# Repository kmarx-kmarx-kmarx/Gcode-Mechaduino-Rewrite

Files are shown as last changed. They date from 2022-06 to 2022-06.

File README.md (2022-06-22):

## Poseidon Prime Firmware and Hardware
Poseidon prime is an open source and low cost syringe pump that uses off-the-shelf parts, 3D printed components, and free software which altogether costs a tenth of other syringe pumps. The design is open-source so anybody can download, modify, and make their own poseidon prime. The syringe pump is highly customizable and can be mounted to rails for extra stability, 3D printed out of polypropylene for heat resistance, and adjusted to fit a variety of syringe sizes. Poseidon prime currently can perform basic fluid dispensing tasks, but going forward it will be able to perform more complex operations and undergo rigorous testing to verify its precision and reliability.

This project builds on [poseidon](https://github.com/pachterlab/poseidon), a project from the Pachter lab. Poseidon prime improves the firmware by adding feedback control and G-code support and builds on the hardware with autoclave-safe polypropylene and a metal shell.

To control poseidon prime, we are using the [Mechaduino](https://github.com/jcchurch13/Mechaduino-Hardware) development board. The Mechaduino repo has the PCB files, BOM, and more information on the project. We found some parts utilized by the Mechaduino project were no longer in stock so we included a new BOM with links to products in stock. 

### The Pump:
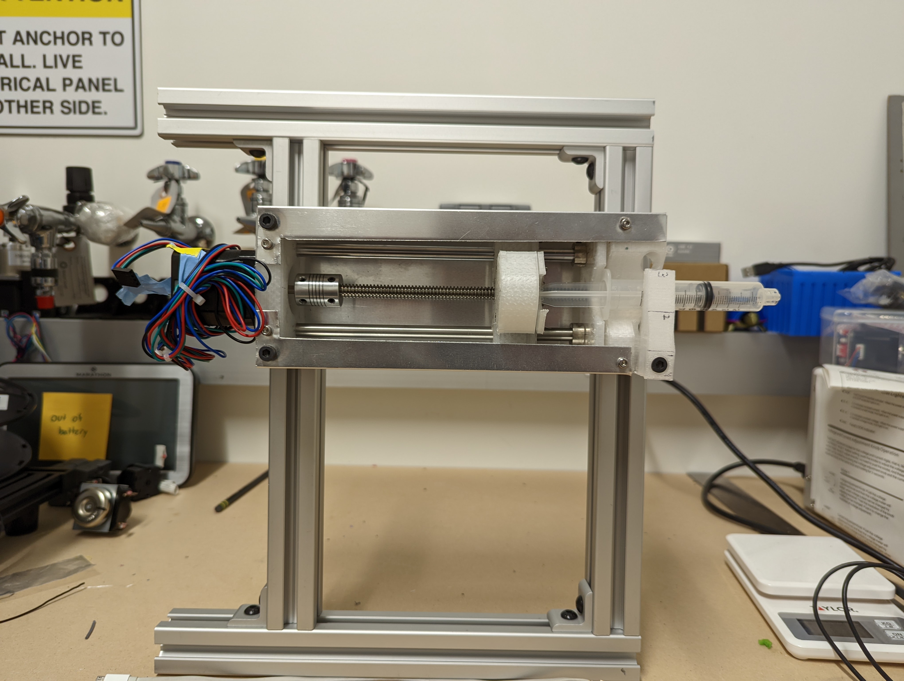
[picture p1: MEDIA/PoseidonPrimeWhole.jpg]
poseidon prime


## What's Included in this Repo
- `Tuning_and_debugging.md`: Guide for tuning and debugging the system
- Supporting Docs
	- `Sine Lookup.ipynb`: Jupyter notebook for generating a sine lookup table
	- `Velocity Lookup.ipynb`: Jupyter notebook for velocity lookup table proof-of-concept
- HARDWARE
	- `poseidon-prime v123.f3z`: Fusion 360 design file for poseidon prime
	- `p_prime_bom.csv`: Bill of Materials for poseidon prime
	- `mecha_bom.csv`: Bill of Materials for Mechaduino.
	- Design Files
		- `p_prime.stl`: STL file for the entire project
		- `back_block.stl`
		- `front_block.stl`
		- `front_clamp.stl`
		- `front_ear_holder.stl`
		- `small_syringe_press.stl`
		- `carriage_block.stl`
		- `carriage_block_cap.stl`
		- `enclosure.dxf`: DXF for the sheet metal enclosure
- Gcode-Mechaduino-Rewrite
	- `pseudocode.txt`: Basic overview of code operation
	- `Gcode-Mechaduino-Rewrite.ino`: Arduino sketch for the project
	- `MagneticEncoder.cpp`, `MagneticEncoder.h`: Files for communicating with the magnetic encoder
	- `MotorCtrl.cpp`, `MotorCtrl.h`: Files for interacting with the motor driver
	- `SerialCommand.cpp`, `SerialCommand.h`: Files for sending and recieving serial communications
	- `ProcessCmd.cpp`, `ProcessCmd.h`: Files for parsing the commands
	- `TimeControlInt.cpp`, `TimeControlInt.h`: Files for initializing and operating the control loops
	- `fastPWM.c`, `fastPWM.h`: Implement a higher frequency PWM
- MEDIA
	- `1CarriageBlockAssembly.mp4`: Video of assembling the carriage block. Perform this step first when building poseidon prime
	- `1CarriageBlockParts.jpg`: Still image of the parts necessary for assembling the carriage block
	- `2FrontBlockParts.jpg`: The parts of the front block
	- `3BackBlockParts.jpg`
	- `4EnclosureParts.jpg`
	- `PoseidonPrimeWhole.jpg`: View of the whole poseidon prime when mounted on rails
	- `PoseidonPrimeTip.jpg`: Close up on syringe end

Poseidon prime uses the Mechaduino microcontroller; see [the Mechaduino project GitHub](https://github.com/jcchurch13/Mechaduino-Hardware) for the BOM.

## Getting Started
### 3D Printing Components and Purchasing Components
See the BOMs for components, estimated prices, and where to purchase. 

The poseidon prime body could be printed in PLA, but PLA will deform and become brittle in an autoclave. It is advised to print usig polypropylene with a relatively high number of walls to ensure no water can enter the blocks. 

### Build Videos
See the [build videos](https://drive.google.com/drive/folders/1_DpoKlkosWUYHRFKvAd-3BIp1i3CB5ML?usp=sharing) for a guide on how to build poseidon prime.

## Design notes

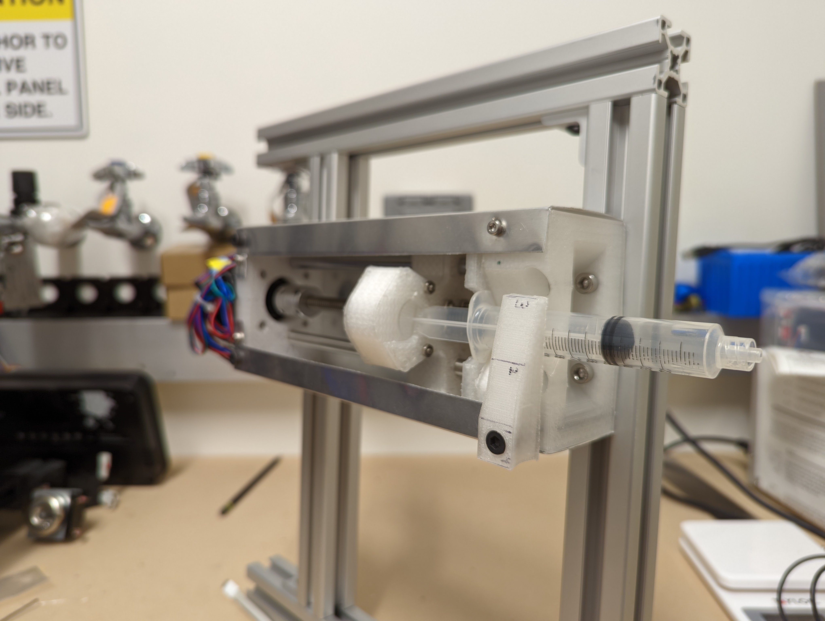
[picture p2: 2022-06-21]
MEDIA/PoseidonPrimeTip.jpg

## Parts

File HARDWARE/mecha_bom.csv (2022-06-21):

Qty (per board) | URL to purchase | Value | Device | Package | Parts | Description
1 | https://www.mouser.com/ProductDetail/onsemi/MBR0520LT1G?qs=3JMERSakebqBWTiPUQp0nw%3D%3D |  | DIODE_SOD-123 | SOD-123 | D1 | Library: MF_Discrete_Semiconductor
4 | DNP |  | HEADER_01X03_PTH_2.54MM | PTH_2.54MM_01X03 | 3V3, GND, V+, VIN | Library: MF_Connectors
1 | DNP |  | HEADER_01X06_PTH_2.54MM | PTH_2.54MM_01X06 | J3 | Library: MF_Connectors
1 | DNP |  | HEADER_01X10_PTH_2.54MM | PTH_2.54MM_01X10 | J2 | Library: MF_Connectors
1 | https://www.mouser.com/ProductDetail/Phoenix-Contact/1935161?qs=W3wJikR1%252BS6eKzfFl8Rbew%3D%3D |  | M025MM | SCREWTERMINAL-5MM-2 | MOTOR_POWER | Standard 2-pin 0.1 header. Use with
1 | https://www.mouser.com/ProductDetail/Amphenol-Commercial-Products/G800W304018EU?qs=f9yNj16SXrKi9QS16pMdvA%3D%3D |  | M04PTH | 1X04 | JP6 | Header 4
1 | https://www.mouser.com/ProductDetail/CK/RKB2SJG250SMTR-LFS?qs=iLbezkQI%252Bsgsc0TY%2FPaT8A%3D%3D |  | TACT_4.2MM | TACT4.2MM | SW2 | Library: MF_Switches
1 | https://www.mouser.com/ProductDetail/Amphenol-FCI/10118193-0001LF |  | USB_MICRO_RIGHT | MICROUSB-RIGHT | J1 | Library: MF_Connectors
2 | https://www.mouser.com/ProductDetail/Susumu/KRL1632E-M-R150-F-T5?qs=B%2FFHBzrwtkbqYiRFE1Q74A%3D%3D | .15 Ohm | R-US_R1206 | R1206 | R12, R13 | RESISTOR
1 | https://www.mouser.com/ProductDetail/Murata-Electronics/GCM155R71H103KA55D?qs=aEuGZpxfbxUFaK62TPaKIA%3D%3D | 0.01uF | CAP0402 | 0402-CAP | C6 | Capacitor
8 | https://www.mouser.com/ProductDetail/Murata-Electronics/GCM155R71A104KA55D?qs=dNBNMwHp2UBmrB9ORE%252B4fA%3D%3D | 0.1uF | CAP0402 | 0402-CAP | C1, C2, C3, C4, C5, C14, C15, C16 | Capacitor
3 | https://www.mouser.com/ProductDetail/Murata-Electronics/GRM155R61C105KA12D?qs=MNX0Jdkv8mRzFdIwfsySnw%3D%3D | 1.0uF | CAP0402 | 0402-CAP | C9, C19 | Capacitor
1 | https://www.mouser.com/ProductDetail/Murata-Electronics/GRT188R61H105KE13D?qs=drgMNd%252BkGPNIxxtJByMGCg%3D%3D | 1.0uF | CAP0603 | 0603-CAP | C13 | Capacitor
1 | https://www.mouser.com/ProductDetail/YAGEO/RC0402FR-13100KL?qs=sGAEpiMZZMvdGkrng054t8AJgcdMkx7x5wItdGYa6aA%3D | 100K | R-US_R0402-VISHAY | R0402-VISHAY | R16 | RESISTOR
1 | https://www.digikey.com/en/products/detail/nichicon/RSA1E101MCN1GS/9452667 | 100uF | CAP_POLD |  | C12 | Capacitor Polarized
8 | https://www.mouser.com/ProductDetail/YAGEO/AC0402JR-0710KL | 10K | R-US_R0402-VISHAY | R0402-VISHAY | R1, R2, R3. R4, R6, R11, R20, R21 | RESISTOR
2 | https://www.mouser.com/ProductDetail/Murata-Electronics/GCM1555C1H180FA16D?qs=QzBtWTOodeXF93Udjj87vw%3D%3D | 18pF | CAP0402 | 0402-CAP | C7, C8 | Capacitor
2 | https://www.mouser.com/ProductDetail/YAGEO/AC0402FR-131KL | 1k | R-US_R0402-VISHAY | R0402-VISHAY | R14, R15 | RESISTOR
1 | https://www.digikey.com/en/products/detail/micro-crystal-ag/CM8V-T1A-32-768KHZ-7PF-20PPM-TA-QC/10499080 | 32768Khz | CRYSTAL2013 | CRYSTAL-SMD-2.0X1.3 | Y1 | Crystal
1 | https://www.mouser.com/ProductDetail/YAGEO/RC0402JR-07330RL | 330 | R-US_R0402-VISHAY | R0402-VISHAY | R5 | RESISTOR
2 | https://www.mouser.com/ProductDetail/YAGEO/RC0402JR-074K7L | 4.7K | R-US_R0402-VISHAY | R0402-VISHAY | R7, R8 | RESISTOR
1 | https://www.mouser.com/ProductDetail/Littelfuse/1206L025YR?qs=PWhpLWeW8wedgRREX8zxcg%3D%3D | 500mA | PTCSMD | PTC-1206 | F1 | Resettable Fuse PTC
1 | https://www.mouser.com/ProductDetail/ams/AS5047D-ATSM | AS5047D | AS5047D | TSSOP14 | U$4
1 | https://www.digikey.com/en/products/detail/allegro-microsystems/A4954ELPTR-T/2509910?lang=en&s=N4IgTCBcDaIIYBYCcBWBIC6BfIA&site=us&x=20&y=17 | AVAGO_DRIVERTHERM | AVAGO_DRIVERTHERM | TSSOP16_THERM | U$1
2 | https://www.digikey.com/en/products/detail/shenzhen-sunlord-electronics-co-ltd/PZ1608U471-1R0TF/14120402 | BLM18PG471SN1D | INDUCTOR0603-TDK | 0603-TDK | L1, L2 | Inductors
4 | https://www.mouser.com/ProductDetail/Nexperia/BSS138P215?qs=A1cBxND5mHJyVAOcRahidg%3D%3D | BSS138 | MOSFET-NCHANNELSMD | SOT23-3 | Q1, Q3, Q4, Q5 | NFET
1 | DNE | FRAME-LEDGER | FRAME-LEDGER | CREATIVE_COMMONS | FRAME1 | Schematic Frame
1 | https://www.mouser.com/ProductDetail/Kingbright/APTD2012LCGCK?qs=AQlKX63v8RvNHN%2F9EGvNTg%3D%3D | Green | 0044_KPT-2012YC | CHIPLED_0805 | LED1 | LED YELLOW - SMD - 0805
1 | DNE | MECHADUINO_LOGO | MECHADUINO_LOGO | MECHADUINO_LOGO | U$5
1 | DNE | NEMA17_HOLE_PATTERNNEW | NEMA17_HOLE_PATTERNNEW | NEMA17_HOLE_PATTERN_2 | U$2
1 | https://www.mouser.com/ProductDetail/Nexperia/2N7002PW115?qs=8%252BCzCWLBsnDY2xJ5Ehsi7w%3D%3D | NFET | MOSFET-NCHANNEL2N7002PW | SOT323 | Q2 | Common NMOSFET Parts
1 | DNE | OSHW-LOGOMOD | OSHW-LOGOMOD | OSHW_LOGO_COPPER_MOD | LOGO4 | Open Source Hardware Logo
1 | https://www.mouser.com/ProductDetail/Microchip-Technology-Atmel/ATSAMD21G18A-AUT | SAMD21G18A-AUT | INTEGRATEDCIRCUITS_1792_SAMD21G18A-AUT | INTEGRATEDCIRCUITS_TQFP48-7X7 | IC1 | Atmel D21 32bit ARM Cortex-M0 microcontroller - 48 PIN TQFP
1 | DNP | SHORT-HA5 | SHORT-HA5 | SHORT_ALL-50 | SH1 | Short between two nets
1 | DNP | SWD | CONNETTORI_0171_PH127-205DF055G00A | CONNETTORI_PINHEAD-2X5-P127 | JP4 | 2x5 PASSO 1
1 | https://www.mouser.com/ProductDetail/STMicroelectronics/LDK130M33RY?qs=1mbolxNpo8eOrhac%2FeIeAA%3D%3D | LDK130M33RY | LDK130M33RY | SOT-23-5 | U1 | 3v3 LDO
1 | DNE | TROPICAL_LABS_LOGO_1LOGO3 | TROPICAL_LABS_LOGO_1LOGO3 | LOGO3 | U$3
1 | https://www.kjmagnetics.com/proddetail.asp?prod=D42DIA&cat=8 | Diametrically magnetized magnet

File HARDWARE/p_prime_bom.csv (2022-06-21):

Quantity | URL to purchase | Cost (USD) | Item | Use | Description
1 | 3D printed | ~ | Back Block | 1x in back block assembly | The back block for connecting to the motor
1 | 3D printed | ~ | Front Block | 1x in front block assembly | The front block for holding the syringe and rails
1 | 3D printed | ~ | Ear Holder | 1x in front block assembly | Holds the ears of the syringe so it doesn't slide along the axis of motion
1 | 3D printed | ~ | Clamp | 1x in front block assembly | Holds the syringe down
1 | 3D printed | ~ | Carriage | 1x in carriage assembly | Presses against the plunger to push liquid out
1 | 3D printed | ~ | Carriage Cap | 1x in carriage assembly | Pulls against the plunger to pull liquid in
1 | https://www.mcmaster.com/8973K298-8973K302/ | $7.90 | 12"x12" Aluminum Sheet 0.0250" Thick | 1x in enclousure | Sheet metal wraps around the whole device for added stability
3 | https://www.mcmaster.com/91292A197 | $1.50 | M5x60 socket head cap screw | 2x in enclosure, 1x in front block | Holds the back block to the rails in the enclosure, attaches the clamp to the front block in the front block assembly
2 | https://www.mcmaster.com/91292A128 | $0.33 | M5x20 socket head cap screw | 2x in enclosure | Holds the front block to the rails
4 | https://www.mcmaster.com/6000N133/ | $5.20 | M5 T-Slotted Framing Fasteners | 4x in enclosure | Holds poseidon prime to the rails
4 |  |  | M3 10 mm socket head cap screw | 4x in enclosure | Holds enclosure sheet metal onto body
4 |  |  | M3 14 mm socket head cap screw | 4x in back block | Holds motor to back block
2 |  |  | M3 20 mm socket head cap screw | 2x in enclosure | Holds enclosure sheet metal onto body
8 |  |  | M3 25 mm socket head cap screw | 8x in carriage | Holds the carriage block and cap together
4 | https://www.mcmaster.com/97259A101/ | $0.32 | M3 low square nut | 4x in enclosure | Holds enclosure sheet metal onto body
6 | https://www.amazon.com/Befenybay-Collar-Shaft-Screw-Printer/dp/B07V41FRZS/ref=sr_1_4?dchild=1 | $5.39 | T8 shaft lock collar | 2x in back block, 4x in front block | Holds rails agaisnt motor in back block, holds rails in place in front block
1 |  |  | Spring | 1x front block | Applies pressure to clamp to hold the syringe in place. It should be roughly 50mm long and slightly larger diameter than the M5 screw
1 |  |  | M5 Nut | 1x front block | Holds the spring in place in the front block
2 |  |  | 200mm long 8mm aluminum rod | 2x front block | The rods the carriage rides on
1 | https://www.amazon.com/uxcell-Stainless-Copper-Thread-Printer/dp/B07R1H5ZMV | $7.25 | 2mm pitch 200mm Threaded rod | 1x carriage | Rotating this rod moves the carriage back and forth
8 |  |  | M3 nut | 8x carriage | Holds the carriage block and cap together
2 |  |  | Brass bushing | 2x carraige | Lets the carriage slide along the rails with low friction

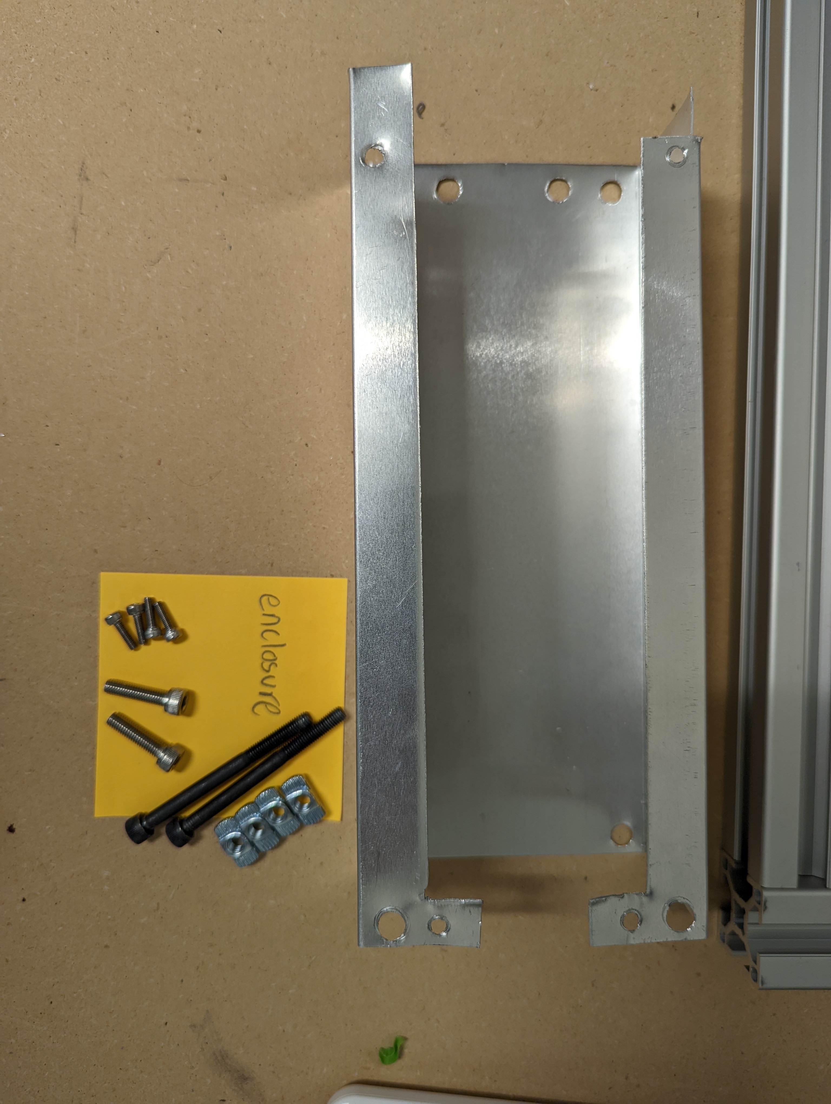
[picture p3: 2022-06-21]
MEDIA/4EnclosureParts.jpg

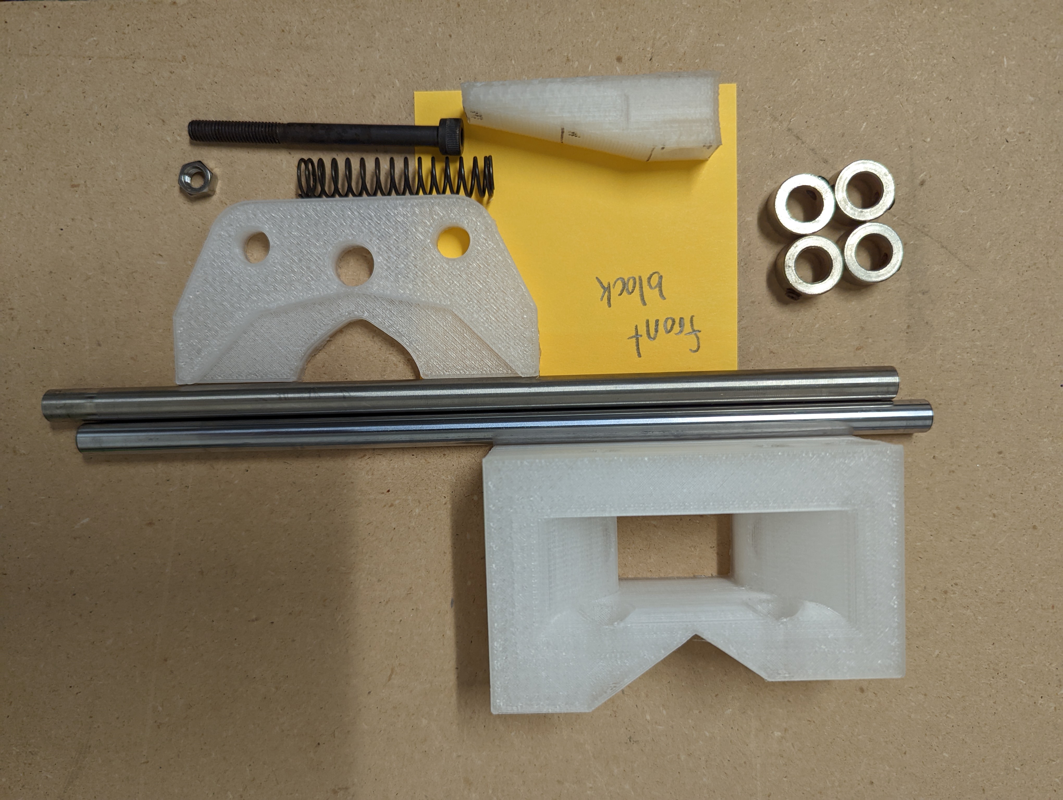
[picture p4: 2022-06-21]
MEDIA/2FrontBlockParts.jpg

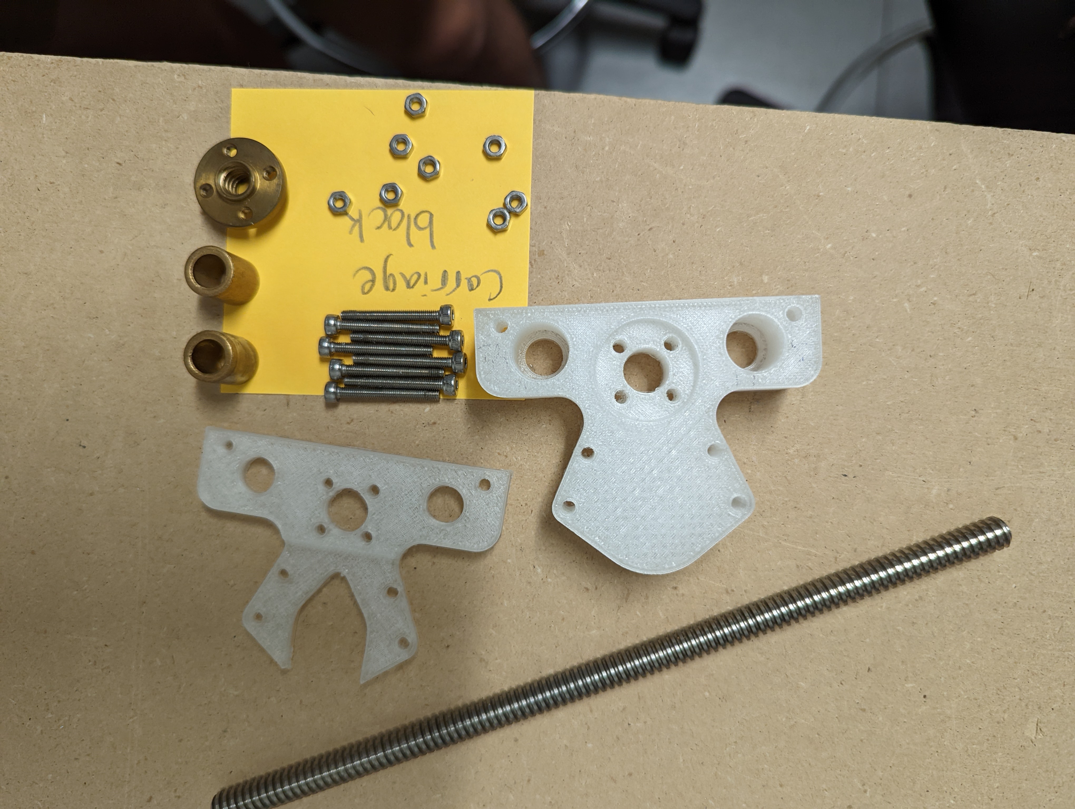
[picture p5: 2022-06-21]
MEDIA/1CarriageBlockParts.jpg

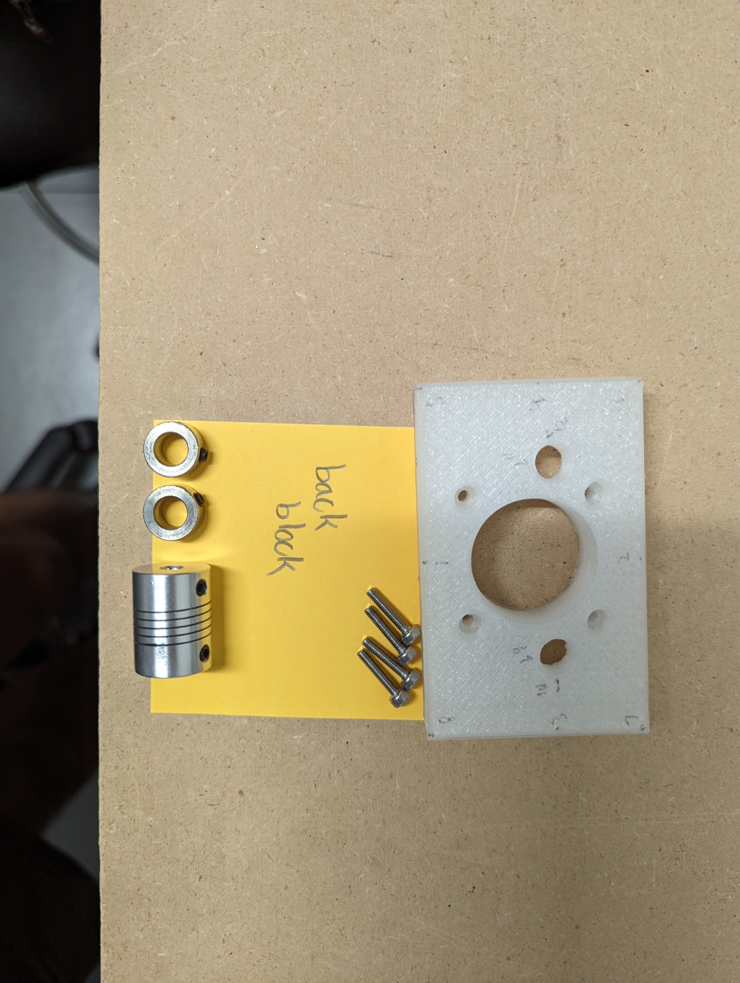
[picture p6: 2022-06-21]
MEDIA/3BackBlockParts.jpg

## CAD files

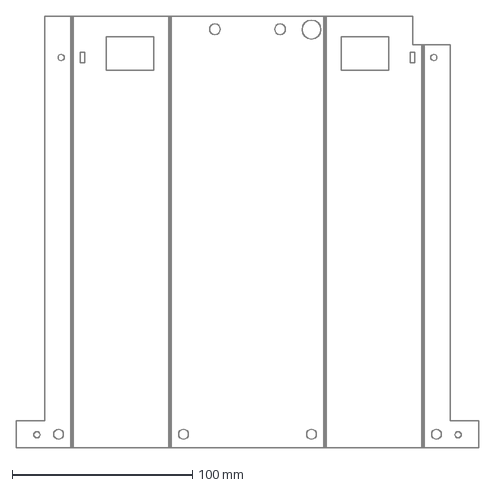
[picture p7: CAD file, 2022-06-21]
HARDWARE/Design Files/enclosure.dxf
256.4 x 239.5 mm

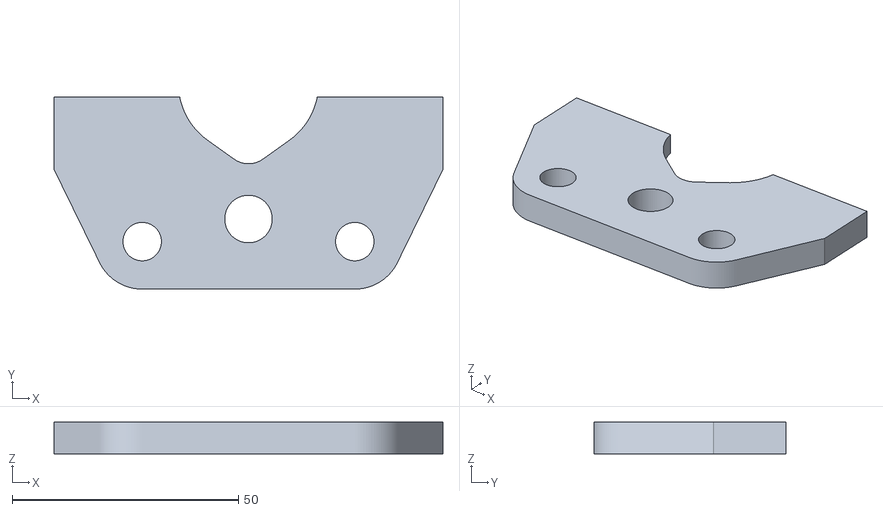
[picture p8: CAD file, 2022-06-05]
HARDWARE/Design Files/front_ear_holder.stl
86.0 x 42.5 x 7.00

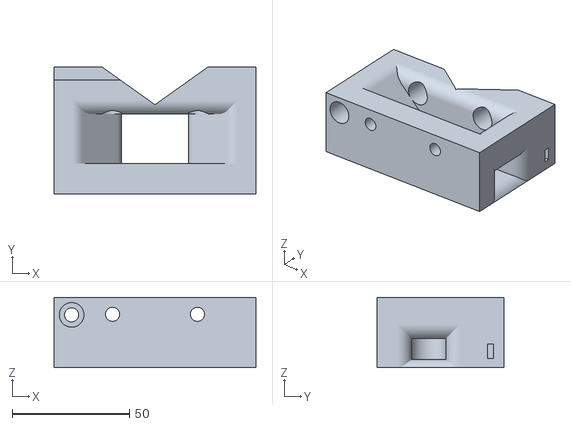
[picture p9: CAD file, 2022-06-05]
HARDWARE/Design Files/front_block.stl
86.0 x 54.0 x 30.0

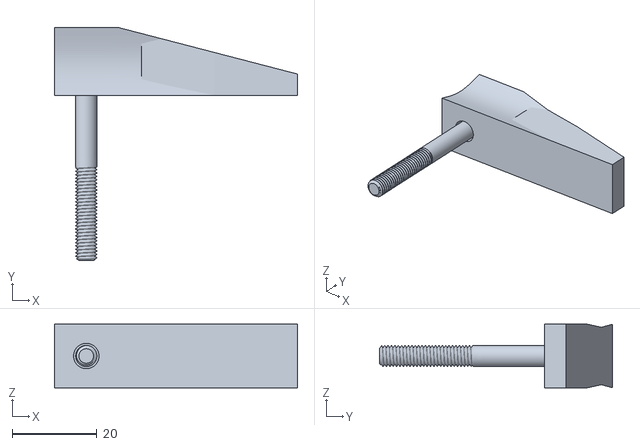
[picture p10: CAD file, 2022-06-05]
HARDWARE/Design Files/front_clamp.stl
57.3 x 55.0 x 15.0

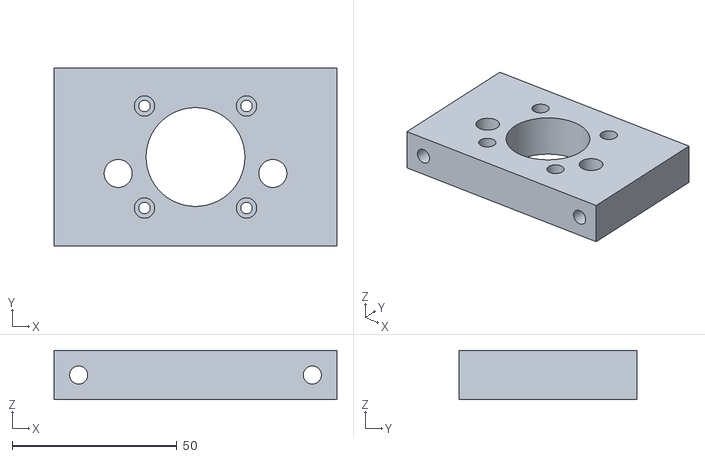
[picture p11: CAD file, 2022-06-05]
HARDWARE/Design Files/back_block.stl
86.0 x 54.0 x 15.0

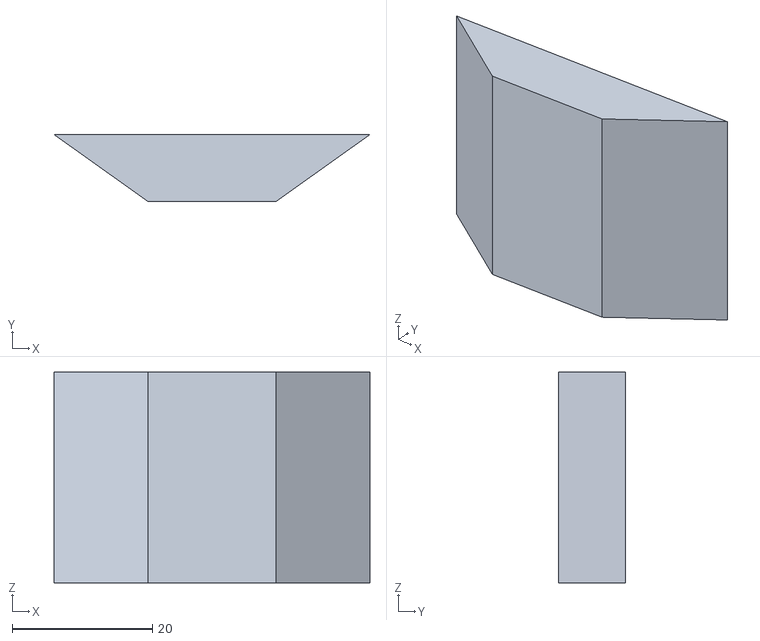
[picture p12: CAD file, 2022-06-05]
HARDWARE/Design Files/small_syringe_press.stl
45.0 x 9.53 x 30.0

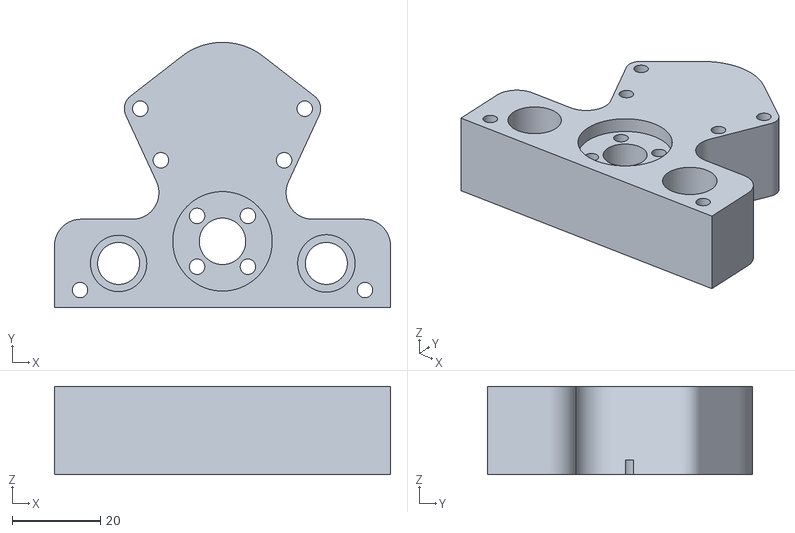
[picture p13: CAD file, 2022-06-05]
HARDWARE/Design Files/carriage_block.stl
76.0 x 60.0 x 20.0

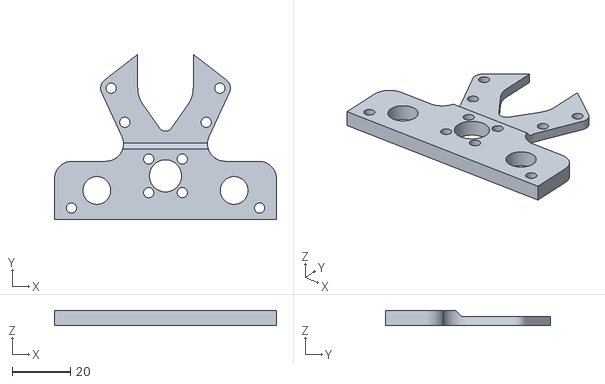
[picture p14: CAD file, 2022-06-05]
HARDWARE/Design Files/carriage_block_cap.stl
76.0 x 56.6 x 5.00

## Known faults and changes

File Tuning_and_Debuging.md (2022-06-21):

# Tuning and Debugging the Gcode-Mechaduino

I fried the Mechaduinos before I could debug and tune them. Here's what I learned on how to *not* fry them, what to do to debug, and how to tune the device parameters once they are functional.

To not fry: always turn off the motor +12V before unplugging the Mechaduino. Having 12V present and the 5V USB not present seems to have caused all my problems.

Now if I hadn't fried it, I would be doing calibration testing. 

## Initial Testing

Un-comment the line `//    SerialUSB.println(precalculated_v[i]);` in ProcessCmd.cpp and upload the code to the Mechaduino.

### Rotation Calibration

First, with everything unplugged, manually jog the carriage to the middle of its travel.

To perform calibration testing, connect the Mechaduino to your computer and send the command "`M111 S1`". This is the "Turn on debugging" command. You will first see the entrie calibration table being spat out and then a message every `DEBUG_DEFAULT` milliseconds indicating various global variables. If this works, turn on the 12V supply. 

Next, run calibration with the command "`G28 A`". `G28` is the normal home command and the `A` modifier is a custom command to instruct a full calibration. This is to match the precedent of 3D printers using the `G28` command to do automatic bed levelling.

When the command is run, the Mechaduino will try to step the motor back and forth to determine if it is wired correctly. Check the Serial port for the error message "`Appears to be backwards`"; if you see this, turn off 12V, unplug the Mechaduino USB, unplug the motor form the Mechaduino, and plug the motor back in with the connector rotated 180 degrees. 

If you do not see this error message, the motor will start stepping through all 200 steps and record the magnetic field at each position. When it is done, it will print "`Done reading`". It next will compute the intermediate values for the steps such that each of the 2^14 values for the magnetic encoder have a "degree" value associated with it. When this is done, it will print "`The calibration table has been written to non-volatile Flash memory!`" to the Serial monitor.

If this fails, check the `calibrate()` function. I'm not sure how it would fail but that's where it would go wrong.

Next, we have to validate the outputs of the calibration. Send "`M111 S1`" again and lok at the new calibration table being printed out. The maximum output value minus the minimum value output should be `VAL_PER_STEP` and the values output should be within some small increment of each other EXCEPT for when it wraps from 0 to `VAL_PER_STEP` or vice versa. 

If the calibration succeeded, we can move on to homing.

### Homing 

Once calibrated and with everything plugged in properly, run "`M111 S1`" and "`G28`". This is the homing instruction; when run without any parameters it will check to see if the rotation calibration occured and will perform that if necessary and then it will perform homing calibration. This again matches the precedent set by 3D printers.

Homing calibration works by putting the device in closed loop mode and running at constant (low) velocity until the carriage hits and end stop. When we hit the end stop, we detect a spike in "effort" and stop, recording the carriage postion. We then go the opposite direction and repeat this operation. 

This operation occurs in closed loop mode and thus depends on our closed loop parameters. Look at the debugging output; we should see the third column (position) increase or decrease linearly with time. The rate of change should also match our set target velocity. If there is any difference or if the velocity is unstable (oscillating, accelerating then decellerating, etc.) then we have to tune the PID parameters. Refer to the Mechaduino maual for guidance on PID tuning. They are under `\\ Parameters for velocity mode` in TimeControlInt.h.

Next, check the fourth and sixth column. The sixth column should be a low pass filtered version of the fourth column. Ensure the sixth column is actual LPF'ed and tacks the actual value without being too noisy. If it is too noisy, make the filter more agressive by increasing `fLPF`. However, we want to make sure we see a rapid rise in filtered effort when we hit the endstops.

If we hit the endstops but fail to detect it and we see our filtered effort is responding properly, use the debug printouts from the filtered effort to set `UNLOADED_EFFORT_LIM`, `UNLOADED_EFFORT_NOM`, and `EFFORT_SLOPE_THRESH`. `UNLOADED_EFFORT_LIM` is the maximum effort we can expend before throwing an error and giving up, `UNLOADED_EFFORT_NOM` is the nominal effort when unloaded, and `EFFORT_SLOPE_THRESH` is the change in filtered effort between timestamps that indicates we are hitting an endstop. These values are all too large; have your hand on the power supply to turn it off when the Mechaduino inevitably runs itself into an endstop and fails to detect it.

Return home by sending "`G28 X`".

### Rapid Move PID

We tuned the velocity PID when doing the homing tests. Next, we tune the positioning PID. Run the command "`G90`" to go to absolute positioning mode, "`G21`" to go to units millimeters, and "`G1 X30`" to move 30 millimeters. It should move rapidly from its current position to 30 mm. If it doesn't move, there's probably something wrong with the timer control. If it moves the wrong amount, there's probably something wrong with the unit conversion. If it moves unusually slowly or starts oscillating, tune the PID controller. 

If this worked, go to units inches and relative positioning mode (`G20` and `G21`) and try moving the carriage around.

### Linear Move Test

If everything else worked, all we have left is the linear move test. Return home, go to units mm, and change mode to absolute positioning and run "`G1 F10`". Nothing should happen. Next, run "`G1 F100 X30`". We should see the carriage accelerate from 10 mm/minute to 100 mm/minute as it moves from its current position to 30mm away. Check the serial monitor to verify the speed is increasing properly.

Try other (positive) feedrates and moving the carriage around its travel. 

If all this works, comment out whatever lines aren't useful, reupload the code, and recalibrate (reuploading wipes calibration data).

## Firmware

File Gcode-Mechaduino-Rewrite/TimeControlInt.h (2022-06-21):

/*
  -----------------------------------------------------------------------------
  DESCRIPTION: This file contains macro definitions and function delcarations for the timer interrupts.
  -----------------------------------------------------------------------------
*/
#include <stdint.h>
#include "MagneticEncoder.h"
#include "MotorCtrl.h"
#include <math.h>

// We want to define this only once
#ifndef __TimeControl_H__
#define __TimeControl_H__
  // Wait until the registers are synchronized
  #define WAIT_TC16_REGS_SYNC(x) while(x->COUNT16.STATUS.bit.SYNCBUSY);

  void setup_TCInterrupts();
  void enable_TCInterrupts();
  void disable_TCInterrupts();

  // Initialize global variables for controlling motor operation
  extern volatile int32_t flags; // Flags, misc. instruction commands
  extern volatile char mode;     // Mode: either positioning(x), velocity (v), or park (neither v nor x)
  extern volatile int32_t u_f;   // IIR-filtered "effort". Filter cutoff freq defined by fLPF
  extern volatile int32_t u_f_1; // The previous value of u_f
  extern volatile int32_t set;   // setpoint, the target position.
  extern volatile int32_t ctrl_start;   // start point of some operation
  extern volatile int32_t ctrl_end;     // end point of some operation  

  // Initialize precomputed velocity table
  #define N_ELEM  256
  extern volatile int32_t precalculated_v[N_ELEM];
  // Define flags bit map
  #define COMMAND_SHIFT  (31-3) // Reserve 3 bits at the top for 2^3 different commands
  #define COMMAND_MASK   (0b111 << COMMAND_SHIFT) // Used to filter out the other bits
  #define NULL_COMMAND    0b000 // Nothing
  #define STOP_COMMAND    0b111 // Halt
  #define MOVE_COMMAND    0b001 // Rapid move
  #define LINEAR_COMMAND  0b010 // Linear move
  #define DWELL_COMMAND   0b011 // Dwell
  #define CMD_READY      0   // Set this bit when there is a command in the command buffer ready to execute
  #define CMD_INVALID    1   // Set this bit if the command was read properly but it is invalid for some other reason
  #define DEBUG_MODE     2   // Set if debugging, clear if you don't want debug messages
  #define POS_ABSOLUTE   3   // Set if absolute positioning, clear if relative
  #define UNITS_MM       4   // Set if in units millimeters, clear if inches
  #define IN_PROGRESS    5   // Set if a command is currently in progress

  // Constants
  #define DIST_THRESH   4*MICROSTEPS // If we are within 4 microsteps of our target, we have hit our target
  

  // Initialize other control global variables
  extern volatile uint32_t U;  //control effort (abs)
  extern volatile int32_t u;  //control effort (not abs)
  extern volatile int32_t r;  //setpoint
  extern volatile int32_t y;  // measured angle
  extern volatile int32_t v;  // estimated velocity (velocity loop)
  extern volatile int32_t yw; // wrapped measured angle
  extern volatile int32_t yw_1; // previous wrapped measured angle
  extern volatile int32_t e;  // e = r-y (error)
  extern volatile int32_t e_1;  // previous error
  
  // Define constants
  // Frequency and Period for the control loop
  #define BASECLK              48000000
  #define TARG_CTRL_LOOP_HZ    6500
  #define CTRL_LOOP_PERIOD     (uint32_t)(BASECLK / TARG_CTRL_LOOP_HZ)
  // Frequency and Period for the command loop
  #define CMD_LOOP_HZ          500
  #define CMD_LOOP_PERIOD      (uint32_t)(BASECLK / (2*CMD_LOOP_HZ)) // divide by 2 to account for clock presale
  // PID loop parameters 
  #define PA                   VAL_PER_STEP       // Target position is 1 step away from current position. Can increase for faster repsonse
  #define ITERM_MAX            (200 * VALS_PER_REV / 360) // Integral term winding limit

  // Parameters for positioning mode:
  // Integral term parameters
  #define pKi          (int32_t)(0.15 * FIXED_PT_SCALE)        // integral error multiplier for abs. positioning mode
  // Differential term parameters
  #define pLPF      30                                            // break frequency in Hz, IIR parameter
  #define pLPFa     (FIXED_PT_SCALE * exp(-2*PI*pLPF/TARG_CTRL_LOOP_HZ)) // scaling factor
  #define pLPFb     FIXED_PT_SCALE-pLPFa                           // scaling factor
  #define pKd       250 * FIXED_PT_SCALE                           // differential error multiplier
  // Proportional term parameters
  #define pKp       15 * FIXED_PT_SCALE          // proportional error multiplier

  // Parameters for velocity mode
  // Integral term parameters
  #define vKi       0.015 * FIXED_PT_SCALE        // integral error multiplier for velocity mode
  // Differential term parameters 
  #define vLPF      100                                 // break frequency in Hz, IIR parameter
  #define vLPFa     (FIXED_PT_SCALE *  exp(-2*PI*vLPF/TARG_CTRL_LOOP_HZ)) // scaling factor
  #define vLPFb     FIXED_PT_SCALE-pLPFa                                             // scaling factor
  #define vKd       0.02 * FIXED_PT_SCALE        // differential error multiplier
  // Proportional term parameters
  #define vKp       0.25 * FIXED_PT_SCALE         // proportional error multiplier
  
  // Filter term parameters
  #define fLPF     0.5 // Break frequency in Hz
  #define fLFPa    (FIXED_PT_SCALE *  exp(-2*PI*vLPF/TARG_CTRL_LOOP_HZ))
  #define fLPFb    FIXED_PT_SCALE - vLPFa

#endif

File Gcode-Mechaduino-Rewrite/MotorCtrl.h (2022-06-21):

/*
  -----------------------------------------------------------------------------
  DESCRIPTION: This file contains macro definitions and function delcarations for setting up and controlling the motor.
  -----------------------------------------------------------------------------
*/
#include <stdint.h>
// We want to define this only once
#ifndef __MOTOR_H__
#define __MOTOR_H__
  // Function declarations
  uint32_t mod(int32_t xMod, int32_t mMod); // modulo function
  void setup_pins();            // Set up pins for motor control
  void stop_motor();            // Park the motor
  int32_t sine_lookup(uint32_t angle);   // Calculate sine from lookup table
  int32_t one_step(bool dir, int32_t step); // Move the motor one step in the specified direction
  void output(int32_t theta, int32_t effort); // Move the motor to the set angle

  // Macros for quickly writing to GPIO
  #define PIN_1_HIGH() (REG_PORT_OUTSET0 = PORT_PA06)
  #define PIN_1_LOW() (REG_PORT_OUTCLR0 = PORT_PA06)
  #define PIN_2_HIGH() (REG_PORT_OUTSET0 = PORT_PA21)
  #define PIN_2_LOW() (REG_PORT_OUTCLR0 = PORT_PA21)
  #define PIN_3_HIGH() (REG_PORT_OUTSET0 = PORT_PA15)
  #define PIN_3_LOW() (REG_PORT_OUTCLR0 = PORT_PA15)
  #define PIN_4_HIGH() (REG_PORT_OUTSET0 = PORT_PA20)
  #define PIN_4_LOW() (REG_PORT_OUTCLR0 = PORT_PA20)
  #define ledPin_HIGH() (REG_PORT_OUTSET0 = PORT_PA17)
  #define ledPin_LOW() (REG_PORT_OUTCLR0 = PORT_PA17)

  // Define global constants
  #define MOTOR_SETTLE     10                 // ms it takes for the motor to settle
  #define STEP_PER_REV     200                // Motor parameter: number of steps
  #define MICROSTEPS       32                 // 1/32 microstepping; we can set the motor to STEPS_PER_REV * QUARTER_TURN possible positions
  #define VALS_PER_REV     (4 * STEP_PER_REV * MICROSTEPS) // Number of "degrees" per full revolution. We want it to be a large number so we can do math as integers without losing precision.
                                                    // We want to make sure we can hit all of the possible values and still have enough resolution for error correction
                                                    // We have 4 bytes (32 bits); 1 revolution takes 15 bits, 1 bit indicates sign, and 8 bits are reserved for fixed point operations. This gives us
                                                    // 256 full revolutions before overflow; for poseidon, we can rotate 100 times before hitting an end stop so this is OK; please tune as needed to meet your needs

  #define FIXED_PT_SCALE   (1<<8) // Increasing this value increases precision but brings us closer to overflowing
  #define VAL_PER_STEP     (int)(VALS_PER_REV/STEP_PER_REV) // Number of "degrees" per step; we have chosen VALS_PER_REV to make this a whole number
  #define QUARTER_TURN     (VALS_PER_REV/4)                 // Number of "degrees" in a quarter of a full rotation
  #define CCW              true                             // Functions as macros for setting motor direction
  #define CW               false
  // Create constant parameters for controlling the motor
  #define iMAX    1.5             // While the A4954 driver is rated for 2.0 Amp peak currents, it cannot handle these currents continuously.  Depending on how you operate the Mechaduino, you may be able to safely raise this value; refer to the A4954 datasheet for more info
  #define rSense  0.150           // Sense resistor resistance in ohms
  #define uMAX    (int32_t)((255/3.3)*(iMAX*10*rSense)) // Set the maximum "effort"; (225 duty/3.3 volts) * (iMax amps * rSense ohms * 10) gives us a way to convert from target current to PWM duty cycle

  // Pin numbers
  #define PIN_4    6   // Pin 1,2,3,4 are motor control pins
  #define PIN_3    5
  #define VREF_2   4   // VREF pins set voltage reference over PWM
  #define VREF_1   9
  #define PIN_2    7
  #define PIN_1    8
  #define ledPin  13  // Built-in LED

  // Device Parameters (for Poseidon)
  // Set by the thread
  #define MM_PER_ROT          2.0
  #define IN_PER_ROT          0.0787402f
  // RPM converted to VALS_PER_REV per minute
  #define DEFAULT_SPEED       (VALS_PER_REV * 10)  // 10 RPM
  #define MIN_SPEED           (VALS_PER_REV / 2048)// 0.00048828125 RPM
  #define MAX_SPEED           (VALS_PER_REV * 310) // 310 RPM

#endif

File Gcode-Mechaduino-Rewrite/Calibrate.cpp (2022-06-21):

/*
  -----------------------------------------------------------------------------
  DESCRIPTION: This file contains the functions necessary to calibrate the motor and write the data to flash storage.
        write_page(): erase the data at shared variable page_ptr and write the data at shared variable page to it

        store_lookup(int lookupAngle): put data into buffer and if the buffer is full, write it to flash

        calibrate(): Step the motor through all positions and save the data

        findijStart(int readings[], int* istart, int* jstart): Find where in the lookup table the reading should go

        wired_correctly(): indicates whether the motor was wired correctly

        calib_home(): Find the maximum and minimum x values of the carriage

  SHARED VARIABLES: Various variables for tracking the flash data.

  GLOBAL VARIABLES: lookup[]: lookup table for encoder-value-to-angle conversions
                    xmin, xmax: the minimum and maximum x values

  INCLUDES:
        MotorCtrl.h: Contains macros and function declarations
        TimeControlInt.h: We need this to turn off the interrupts
        MagneticEncoder.h: For macros and encoder reading functions
        Arduino.h: Has macros and definitions for the board
        stdint.h:  Definitions for integer types
  -----------------------------------------------------------------------------
*/


#include <FlashStorage.h>
#include "MagneticEncoder.h"
#include "MotorCtrl.h"
#include "TimeControlInt.h"
#include "Calibrate.h"
#include <Arduino.h>

// Initialize position global variables
int32_t xmin = 0;
int32_t xmax = 0;

// Initialize lookup table with 2^14 elements, one for each possible encoder value
extern const uint32_t __attribute__((__aligned__(256))) lookup[16384] = {};

// Initialize flash parameters
static FlashClass flash;               // Create new flash object

static uint32_t page_count;

static int32_t page[INTS_PER_PAGE];        // Buffer everthing that will be stored in ram
static const void * page_ptr;              // Pointer to flash page

/*
  -----------------------------------------------------------------------------
  DESCRIPTION: write_page() writes the page buffer to flash storage.

  OPERATION:   We first erase the page that page_ptr points to and then we write page to page_ptr.

  ARGUMENTS/RETURNS: none

  INPUTS / OUTPUTS: None

  LOCAL VARIABLES: None

  SHARED VARIABLES: void * page_ptr: This void points to the start of the flash page we want to write to
                    int page[]: This is the page buffer array 

  GLOBAL VARIABLES: None

  DEPENDENCIES:
        FlashStorage.h:  has definitions for flash manipulations.
  -----------------------------------------------------------------------------
*/
static void write_page() {
  flash.erase((const void*) page_ptr, sizeof(page));
  flash.write((const void*) page_ptr, (const void *) page, sizeof(page));
  return;
}

/*
  -----------------------------------------------------------------------------
  DESCRIPTION: store_lookup(int32_t lookupAngle) stores data to either the page buffer or flash.

  OPERATION:   We add the lookupAngle to our page buffer. Then, if the page buffer is full, we write the page, reset the buffer, and index the page pointer.

  ARGUMENTS:   int32_t lookupAngle: the angle to store

  RETURNS:     None

  INPUTS / OUTPUTS: None

  LOCAL VARIABLES: None

  SHARED VARIABLES: int page_count: This is our index of the page buffer array
                    int page[]: This is the page buffer array 
                    void * page_ptr: This void points to the start of the flash page we want to write to

  GLOBAL VARIABLES: None

  DEPENDENCIES:
        FlashStorage.h:  has definitions for flash manipulations.
  -----------------------------------------------------------------------------
*/
static void store_lookup(int32_t lookupAngle) {
  // Add angle to the page
  page[page_count++] = lookupAngle;
  // If we don't have a full page, return
  if(page_count < INTS_PER_PAGE){
    return;
  }

  // we've filled an entire page, write it to the flash
  write_page();

  // reset our counters and increment our flash page
  page_ptr = (char*)page_ptr + sizeof(page); // cast to char to adhere to GCC standard
  page_count = 0;
  memset(page, 0, sizeof(page));
}
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

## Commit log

2022-02-23 Incremental additions to calibrate; code re-organized
2022-03-14 Incremental optimizations and additions to calibrate
2022-04-20 Implemented debug data printing
2022-06-05 Added STLs
    [back_block.stl, carriage_block.stl, carriage_block_cap.stl, enclosure.dxf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]
2022-06-21 added docs
    [enclosure.dxf, mecha_bom.csv, p_prime_bom.csv]
2022-06-21 added assembly photos
